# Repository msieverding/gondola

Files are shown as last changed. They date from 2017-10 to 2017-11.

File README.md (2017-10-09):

# gondola
## A parametric robot infrastructure for repeatable mobile experiments

This gondola was developed during a projet thesis at Graz University of Technology. This repository contains the following four main parts:
- Application Code for ESP8266 (/esp8266_controller)
- Printed circuit board (/esp8266_pcb)
- Some documentation and evaluation in .xls and .m files (/doc)
- 3D printed parts for this gondola (/3d_parts) copied from https://github.com/iprotonotarios/gondola

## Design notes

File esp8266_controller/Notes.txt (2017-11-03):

TODO:
- check all TODOs
- implement state for SW LED
- Application:
    - Add more freedom for applications, like section in EEPROM for configuration

Ideas:
- Use NTP for a time (maybe good for debug output, etc..). NTP is used here (https://github.com/Azure/azure-iot-arduino-protocol-http/blob/master/examples/simplesample_http/simplesample_http.ino)

Out of code documentation:
- Setup ATOM build environment
- Add libraries (https://www.youtube.com/watch?v=EBlHNBNHESQ)
- compiler optiization -O3 for maxium speed. Size does not matter on this chip

Unused libraries:
- PubSubClient
- AsyncMqttClient (https://github.com/marvinroger/async-mqtt-client)
  - 11.09.2017: Client recieves multiple messages and crashes.
  - MqTT server is very bad and neither server nor client fully supports QoS 2 and 3
- MqTT Server for ESP8266: https://github.com/FrancescoBaroneItaly/ME-MqTT-Server-for-ESP8266
  - Necessary to install certain libraries. They will show up as errors while building :D
  - Tutorial: http://bartech.mybluemix.net/2017/07/19/me-project-setup-mqtt-server-instance-on-esp8266/#more-828
- async MqTT Client used in MQTTClientAsync: (https://github.com/marvinroger/async-mqtt-client)
- use json? - JSON writer (https://github.com/maxpowel/ArduinoJsonWriter/blob/master/JsonWriter.cpp)
  - Unnecessary overhead -> not used. Binary protocoll

Used libraries:
- WebSocket Server and Cient (https://github.com/Links2004/arduinoWebSockets?utm_source=platformio&utm_medium=piohome)
 - Can use AsyncTCP with :https://github.com/me-no-dev/ESPAsyncTCP
 - see in readme of https://github.com/Links2004/arduinoWebSockets?utm_source=platformio&utm_medium=piohome
 - flag can be set in compiler (see platformio.ini)

Usefull sources:
- Linear regression: https://de.mathworks.com/help/matlab/data_analysis/linear-regression.html
- Paper about movement to optimize things: https://repository.tudelft.nl/islandora/object/uuid:aaecae50-6b30-40c3-accf-53302d200656/datastream/OBJ
- Exception decoder https://github.com/me-no-dev/EspExceptionDecoder

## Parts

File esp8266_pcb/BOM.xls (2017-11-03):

BOM – Gondola | No PCB's: | 3
Unit | per PCB | fixed | Total | Mouser Part No | Link
C1 | 1 | 0 | 3 | 667-EEE-FPV101XAP | http://www.mouser.at/ProductDetail/Panasonic/EEE-FPV101XAP/?qs=d1CqaRUMZD%2fZv%252bRM%2f4gWcQ%3d%3d
D1 | 1 | 0 | 3 | 821-1N4004 | http://www.mouser.at/ProductDetail/Taiwan-Semiconductor/1N4004/?qs=sGAEpiMZZMuMAfj%252bWfX4nEEHllp3mZcc
F1 | 1 | 0 | 3 | 652-MFR500 | http://www.mouser.at/ProductDetail/Bourns/MF-R500/
JP1 | 1 | 0 | 3 | 538-90131-0123 | http://www.mouser.at/ProductDetail/Molex/90131-0123/
Jumper | 3 | 0 | 9 | 571-530153-2 | http://www.mouser.at/ProductDetail/TE-Connectivity-AMP/530153-2/
LED | 5 | 0 | 15 | 604-APTD2012LQBCD | http://www.mouser.at/ProductDetail/Kingbright/APTD2012LQBC-D/
R1, R2 4,7k | 2 | 0 | 6 | 71-CRCW0805-4.7K-E3 | http://www.mouser.at/ProductDetail/Vishay/CRCW08054K70FKEA/
R3 1,2k | 1 | 0 | 3 | 756-PCF0805131K2BT1 | http://www.mouser.at/ProductDetail/Welwyn-Components-TT-Electronics/PCF0805-13-1K2BT1/
R4, R5 330 | 2 | 0 | 6 | 71-TNPW0805330RBEEA | http://www.mouser.at/ProductDetail/Vishay/TNPW0805330RBEEA/
R6, R7 100k | 2 | 0 | 6 | 588-AS08J1003ET | http://www.mouser.at/ProductDetail/Ohmite/AS08J1003ET/
S1 | 1 | 0 | 3 | 506-FSMCTTR | http://www.mouser.at/ProductDetail/TE-Connectivity-Alcoswitch/FSMCTTR/
A4988BREAKOUT | 1 | 0 | 3 |  | https://www.pololu.com/product/2133
A4899 Socket | 2 | 0 | 6 | 538-90147-1108 | http://www.mouser.at/ProductDetail/Molex/90147-1108/
ADAFRUIT_ESP8266 | 1 | 0 | 3 | 485-2471 | http://www.mouser.at/ProductDetail/Adafruit/2471/
ESP8266 Socket | 2 | 0 | 6 | 538-90147-1110 | http://www.mouser.at/ProductDetail/Molex/90147-1110/
DC DC | 1 | 0 | 3 | 755-BP5293-50 | http://www.mouser.at/ProductDetail/ROHM-Semiconductor/BP5293-50/
X1 | 1 | 0 | 3 | 651-1751248 | http://www.mouser.at/ProductDetail/Phoenix-Contact/1751248/
X2 | 1 | 0 | 3 | 651-1751264 | http://www.mouser.at/ProductDetail/Phoenix-Contact/1751264/
FTDI | 0 | 1 | 1 | 485-954 | http://www.mouser.at/ProductDetail/Adafruit/954/?qs=sGAEpiMZZMsMyYRRhGMFNg7907eNh002i%2fEnSsNEsb4%3d
Power Supply | 0 | 1 | 1 | 923-96PSAA36W12R1 | http://www.mouser.at/ProductDetail/Advantech/96PSA-A36W12R1/
Power Supply Cable | 0 | 1 | 1 | 364012-01 | http://www.mouser.at/ProductDetail/Qualtek/364012-01/?qs=sGAEpiMZZMvXcJVS4l7FP55o5eU9S9b7yWO1vi9Pexw%3d

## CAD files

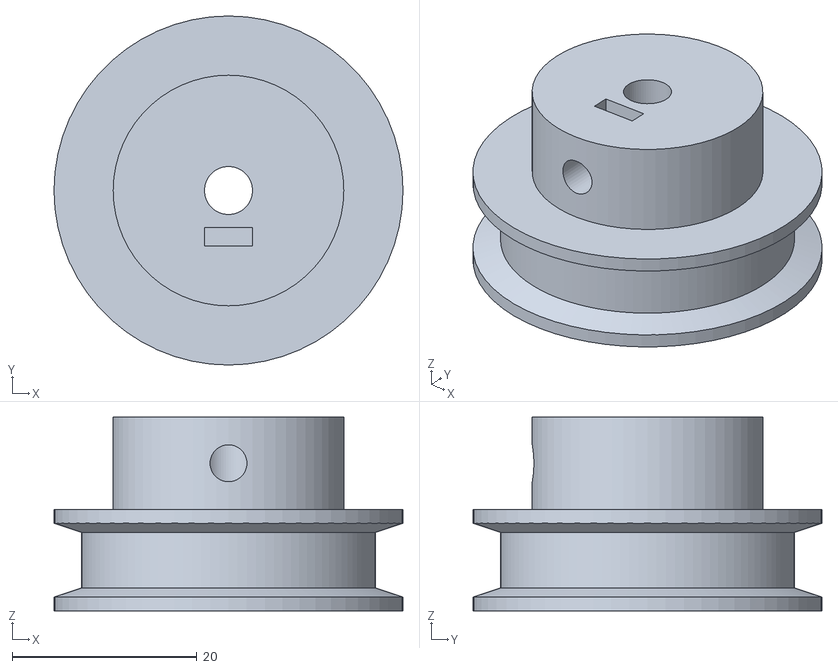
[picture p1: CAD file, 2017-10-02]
3d_parts/nema17_pulley.stl
37.8 x 37.8 x 21.0

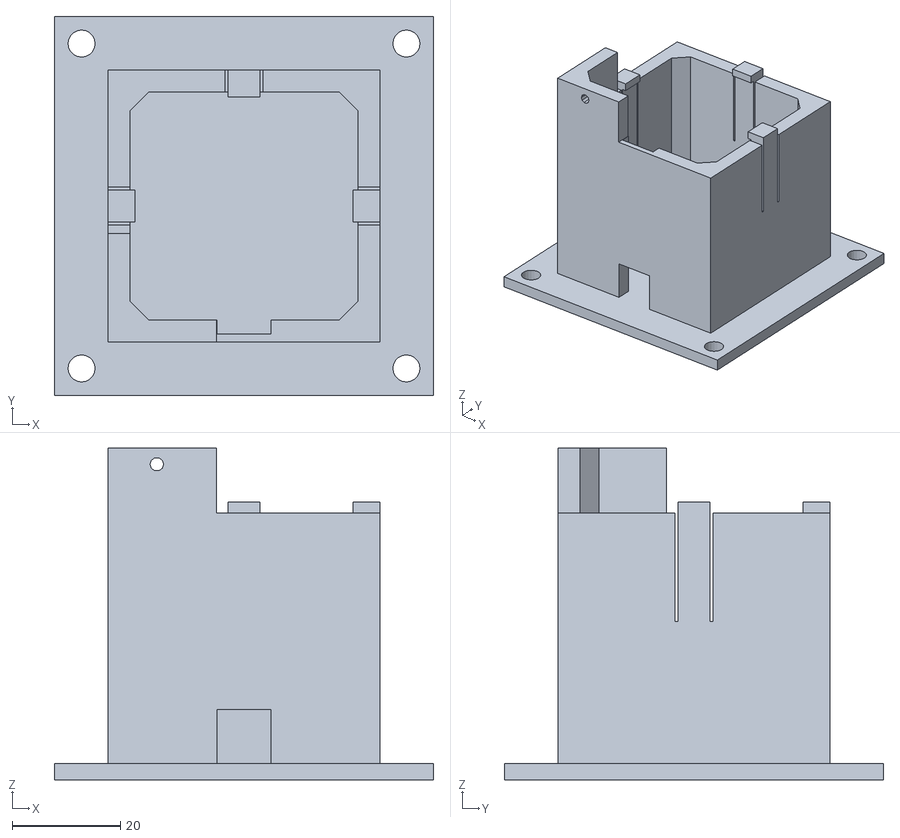
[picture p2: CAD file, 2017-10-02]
3d_parts/nema17_motor_base.stl
70.0 x 70.0 x 61.3

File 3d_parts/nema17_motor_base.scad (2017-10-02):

motorSide = 42.2;
motorHeight = 46.3;
motorMountingHoles = 31;
motorHolesLength = 4.5;

baseSide = 70;
baseHeight = 3;

wallWidth = 4;

// mounting base plate
difference()
{
    cube([baseSide, baseSide, baseHeight]);
    
    translate([5, 5, 0]) cylinder(d=5, h=baseHeight, $fn=20);
    translate([baseSide-5, 5, 0]) cylinder(d=5, h=baseHeight, $fn=20);
    translate([5, baseSide-5, 0]) cylinder(d=5, h=baseHeight, $fn=20);
    translate([baseSide-5, baseSide-5, 0]) cylinder(d=5, h=baseHeight, $fn=20);
    
}
// main enclosure
translate([(baseSide-motorSide)/2-wallWidth, (baseSide-motorSide)/2-wallWidth, baseHeight])
{
    difference()
    {
        union()
        {
            cube([motorSide+wallWidth*2, motorSide+wallWidth*2, motorHeight]);
            translate([0, 0, motorHeight])
            {
               difference()
               {
                   // thread hole and support
                   cube([20, 20, 12]);
                   translate([9, 0, 9]) rotate([-90, 0, 0]) cylinder(d=2.5, h=10, $fn=10);
               }
           }
       }
   
        
        translate([wallWidth+sqrt(2)*2.5, wallWidth, 0])
            minkowski()
            {
                cube([motorSide-sqrt(2)*5, motorSide-sqrt(2)*5, motorHeight]);
                rotate([0, 0, 45]) cube([5, 5, motorHeight]);
            }
         
        // latches   
        translate([motorSide/2+wallWidth-3.5, motorSide+wallWidth, motorHeight-20])        
            cube([0.5, wallWidth, 20]);
        translate([motorSide/2+wallWidth+3, motorSide+wallWidth, motorHeight-20])
            cube([0.5, wallWidth, 20]);
            
        translate([0, motorSide/2+wallWidth-3.5, motorHeight-20])
            cube([wallWidth, 0.5, 20]);
        translate([0, motorSide/2+wallWidth+3, motorHeight-20])
            cube([wallWidth, 0.5, 20]);
            
        translate([motorSide+wallWidth, motorSide/2+wallWidth-3.5, motorHeight-20])
            cube([wallWidth, 0.5, 20]);
        translate([motorSide+wallWidth, motorSide/2+wallWidth+3, motorHeight-20])
            cube([wallWidth, 0.5, 20]);
       
        // wire hole
        translate([motorSide/2+wallWidth-5, 0, 0])
            cube([10, wallWidth, 10]);
            
        // wire shaft
        translate([motorSide/2+wallWidth-5, wallWidth-2.5, 0])
            cube([10, 2.5, motorHeight]);
    }
    
    // latches top
    translate([motorSide/2+wallWidth-3, motorSide+wallWidth-1, motorHeight])
        cube([6, wallWidth+1, 2]);
    translate([0, motorSide/2+wallWidth-3, motorHeight])
        cube([wallWidth+1, 6, 2]);    
    translate([motorSide+wallWidth-1, motorSide/2+wallWidth-3, motorHeight])
        cube([wallWidth+1, 6, 2]);    
  
}

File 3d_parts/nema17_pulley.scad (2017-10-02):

innerDiameter = 2*50/PI;
outerDiameter = innerDiameter+6;

outerHeight = 11;
innerHeight = 8;
stepperShaftDiameter = 5.2; // default is 5, due to over-extrusion we had to change this; act accordingly 

//main pulley body
difference(){
    cylinder(d=outerDiameter, h=outerHeight, $fn=60);
    cylinder(d=stepperShaftDiameter, h=outerHeight, $fn=60);
    
    translate([0, 0, outerHeight/2-innerHeight/2]){
            
        difference(){
            translate([-outerDiameter/2, -outerDiameter/2, 0]) cube([outerDiameter, outerDiameter, innerHeight]);
            
            cylinder(r2=innerDiameter/2, r1=outerDiameter/2, h=1, $fn=100);
            translate([0, 0, 1]) cylinder(r=innerDiameter/2, h=innerHeight-2, $fn=100);
            translate([0, 0, innerHeight-1]) cylinder(r1=innerDiameter/2, r2=outerDiameter/2, h=1, $fn=100);
        }
    }
}

// locking screw and nut
translate([0, 0, outerHeight])
{
    difference()
    {
        cylinder(d=25, h=10, $fn=60);
        cylinder(d=stepperShaftDiameter, h=10, $fn=60);
        
        translate([0, 0, 5]) rotate([90, 0, 0]) cylinder(d=4, h=15, $fn=40);
        translate([-2.6, -6, 2.5]) cube([5.2, 2, 10]); 
    }
}

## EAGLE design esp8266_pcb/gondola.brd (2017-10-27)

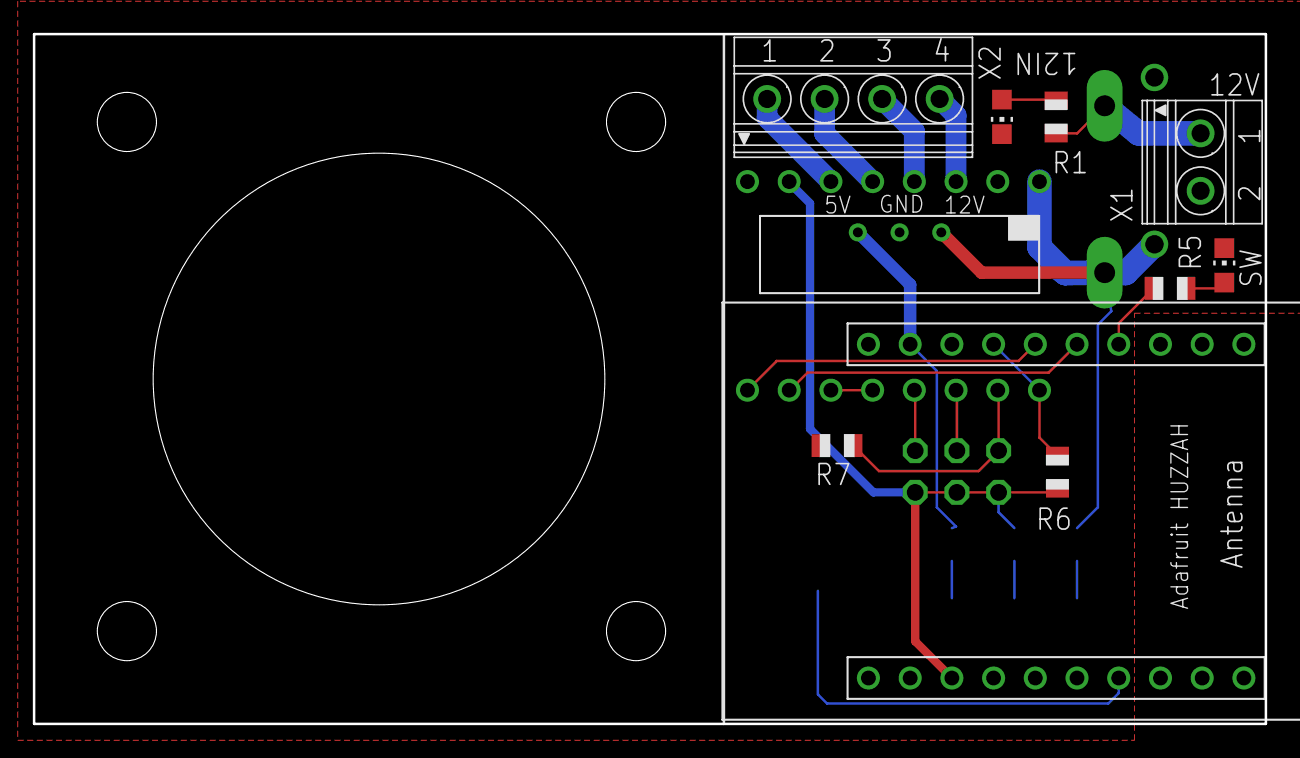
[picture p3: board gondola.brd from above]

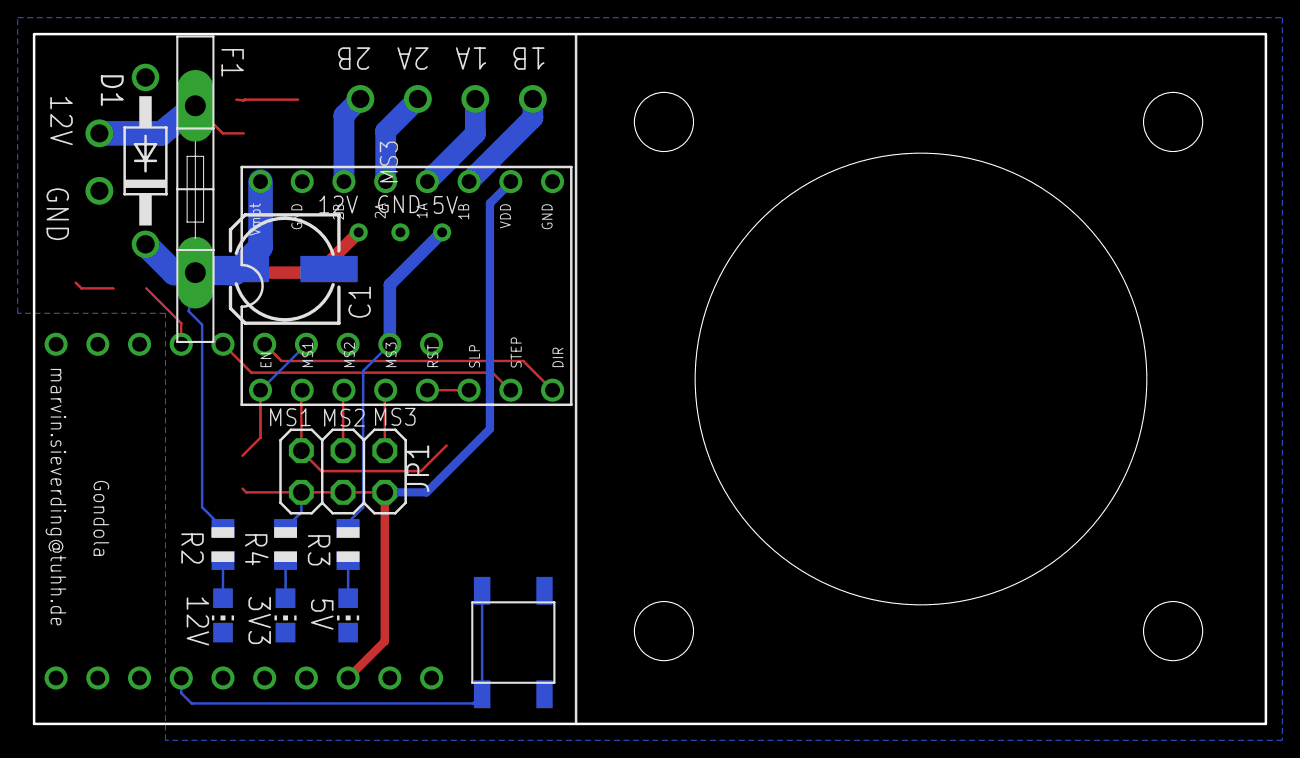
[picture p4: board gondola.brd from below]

Board: 2 copper layers, 75.0 x 42.0 mm, 22 parts (12 on the bottom side), 23 nets.

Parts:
C1: 100µF; 153CLV-0605
D1: 1N4004; DO41-10
F1: MFR500
JP1: 2X03
LED1_12IN, LED2_12V, LED3_5V, LED4_3V3, LED5_SW: CHIP-LED0805
R1, R2: 4.7k; R0805
R3: 1.2k; R0805
R4, R5: 330; R0805
R6, R7: 100k; R0805
U1: ROHM_BP5293-XX
U$1: A4988BREAKOUT
U$2: ADAFRUIT_ESP8266
U$4: FSMCTTR
X1: 1751248
X2: 1751264

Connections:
1A: U$1.1A, X2.2
1B: U$1.1B, X2.1
2A: U$1.2A, X2.3
2B: U$1.2B, X2.4
12V_IN: F1.P$1, R1.2, X1.1
!RESET: U$1.RST, U$1.SLP
+3V3: JP1.1, JP1.3, JP1.5, R4.2, R6.1, U$1.VDD, U$2.3_3V3
+5V: R3.2, U1.VOUT, U$2.9_VBAT
+12V: C1.+, D1.C, F1.P$2, R2.2, U1.VIN, U$1.VMOT
DIR: U$1.STEP, U$2.5_GPIO14
GND: C1.-, D1.A, LED1_12IN.C, LED2_12V.C, LED3_5V.C, LED4_3V3.C, LED5_SW.C, R7.2, U1.GND, U$1.GND, U$1.GND@0, U$2.1_GND, U$2.10_GND, U$4.1, U$4.2, X1.2
MS1: JP1.2, R7.1, U$1.MS1
MS2: JP1.4, U$1.MS2
MS3: JP1.6, U$1.MS3
M_EN: R6.2, U$1.EN, U$2.7_GPIO13
unnamed: LED2_12V.A, R2.1
unnamed: LED1_12IN.A, R1.1
unnamed: LED4_3V3.A, R4.1
unnamed: LED5_SW.A, R5.1
unnamed: LED3_5V.A, R3.1
STEP: U$1.DIR, U$2.6_GPIO12
SW_BUT: U$2.7_GPIO4, U$4.3, U$4.4
SW_LED: R5.2, U$2.4_GPIO16

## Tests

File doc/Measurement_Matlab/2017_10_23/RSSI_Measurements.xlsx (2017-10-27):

Algorithm 1 - Sampling
x | y | RSSI
RUN | 1
40 | 50 | -55
40 | 150 | -62
40 | 250 | -49
40 | 225 | -53
40 | 250 | -51
40 | 275 | -55
40 | 250
RUN | 2
40 | 50 | -55
40 | 150 | -50
40 | 250 | -48
40 | 225 | -47
40 | 250 | -49
40 | 275 | -58
40 | 225
Algorithm 2 - Random Walk
RUN | 1
40 | 225 | -50
40 | 215 | -49
40 | 205 | -48
40 | 195 | -50
40 | 205 | -49
40 | 215 | -48
40 | 225 | -49
40 | 215
40 | 215 | -47
40 | 205 | -49
40 | 215 | -47
40 | 225 | -49
40 | 215
40 | 50 | -55
40 | 40 | -56
40 | 50 | -57
40 | 60 | -52
40 | 70 | -52
40 | 80 | -52
40 | 90 | -59
40 | 80
40 | 80 | -52
40 | 70 | -49
40 | 60 | -52
40 | 70 | -49
40 | 80 | -56
40 | 70
Algorithm 1 - Sampling with better grid
RUN 1
40 | 50 | -56
40 | 100 | -59
40 | 150 | -52
40 | 200 | -51
40 | 250 | -50
40 | 225 | -48
40 | 240 | -49
40 | 250 | -49
40 | 260 | -49
40 | 275 | -55
40 | 225
RUN 2
40 | 50 | -56
40 | 100 | -54
40 | 150 | -57
40 | 200 | -49
40 | 250 | -48
40 | 225 | -49
40 | 240 | -48
40 | 250 | -49
40 | 260 | -53
40 | 275 | -50
40 | 240

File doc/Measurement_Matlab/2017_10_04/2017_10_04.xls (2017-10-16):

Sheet: 01
Offset X | 2364 | Offset Y | 1200 |  | 2D Messung als verifizierung des codes
Punkt | X | Y | Meas X | Meas Y | Dist X | Dist Y | Err X | Err Y | abs(Err)
0 | 400 | 1500 | 1964 | 2700 | 400 | 1500 | 0 | 0 | 0.00
1 | 400 | 1200 |  |  | 405 | 1798 | -5 | 598 | 598.02
2 | 400 | 900 |  |  | 2364 | -1200 | -1964 | -2100 | 2875.29
3 | 400 | 600 |  |  | 2364 | -1200 | -1964 | -1800 | 2664.08
4 | 400 | 300 |  |  | 2364 | -1200 | -1964 | -1500 | 2471.29
5 | 400 | 1800 | 1959 | 2998 | 405 | 1798 | -5 | -2 | 5.39
6 | 400 | 2100 | 1967 | 3294 | 397 | 2094 | 3 | -6 | 6.71
7 | 400 | 2400 | 1969 | 3595 | 395 | 2395 | 5 | -5 | 7.07
8 | 400 | 2700 |  |  | 2364 | -1200 | -1964 | -3900 | 4366.61
9 | 400 | 3000 |  |  | 2364 | -1200 | -1964 | -4200 | 4636.52
10 | 800 | 1500 |  |  | 2364 | -1200 | -1564 | -2700 | 3120.27
11 | 800 | 1200 |  |  | 2364 | -1200 | -1564 | -2400 | 2864.63
12 | 800 | 900 |  |  | 2364 | -1200 | -1564 | -2100 | 2618.41
13 | 800 | 600 |  |  | 2364 | -1200 | -1564 | -1800 | 2384.55
14 | 800 | 300 |  |  | 2364 | -1200 | -1564 | -1500 | 2167.05
15 | 800 | 1800 |  |  | 2364 | -1200 | -1564 | -3000 | 3383.21
16 | 800 | 2100 |  |  | 2364 | -1200 | -1564 | -3300 | 3651.86
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

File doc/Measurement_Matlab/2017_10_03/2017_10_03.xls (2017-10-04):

OffsetX | 2364
OffsetY | 1200
OffsetZ | 5
crash
1 | startMeas | start | Input | endMeas | end
x | 1618 | 746 | 746 | 1607 | 757 | 11
y | 3686 | 2486 | 1486 | 2691 | 1491 | 5
z | 759 | 754 | 745 | 761 | 756 | 11
2 | startMeas | start | Input | endMeas | end
x | 1607 | 757 | 746 | 1557 | 807 | 61
y | 2691 | 1491 | 1486 | 1487 | 1487 | 1
z | 761 | 756 | 1745 | 1760 | 1755 | 10
3 | startMeas | start | Input | endMeas | end
x | 1557 | 807 | 807 | 1579 | 785 | -22
y | 1487 | 1487 | 487 | 506 | 506 | 19
z | 1760 | 1755 | 1755 | 1763 | 1758 | 3
4 | startMeas | start | Input | endMeas | end
x | 1579 | 785 | 785 | 1571 | 793 | 8
y | 506 | 506 | 1006 | 995 | 995 | -11
z | 1763 | 1758 | 1758 | 1767 | 1762 | 4
5 | startMeas | start | Input | endMeas | end
x | 1571 | 793 | 793 | 1585 | 779 | -14
y | 995 | 995 | 995 | 984 | 984 | -11
z | 1767 | 1762 | 2762 | 2769 | 2764 | 2
6 | startMeas | start | Input | endMeas | end
x | 1585 | 779 | 779 | 1597 | 767 | -12
y | 984 | 984 | 984 | 2147 | 947 | -37
z | 2769 | 2764 | 3764 | 3759 | 3754 | -10
7 | startMeas | start | Input | endMeas | end
x | 1597 | 767 | 767 | 1584 | 780 | 13
y | 2147 | 947 | 1947 | 3121 | 1921 | -26
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

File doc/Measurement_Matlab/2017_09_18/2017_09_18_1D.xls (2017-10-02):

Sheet: 01
1D Measurements
Spooled mm | Speed cm/s | Meas 1 mm | Meas 2 mm | Meas 3 mm | Mean mm | Distance Total | Err Total mm | Err %target traveled distance
0 |  | 1248 | 1248 | 1248 | 1248.0 | 0.00 | 0.00
100 | 5 | 1150 | 1149 | 1148 | 1149.0 | 99.00 | -1.00 | -1.00%
200 | 5 | 1047 | 1047 | 1047 | 1047.0 | 201.00 | 1.00 | 0.50%
300 | 5 | 946 | 946 | 945 | 945.7 | 302.33 | 2.33 | 0.78%
400 | 5 | 844 | 844 | 844 | 844.0 | 404.00 | 4.00 | 1.00%
500 | 5 | 741 | 742 | 741 | 741.3 | 506.67 | 6.67 | 1.33%
600 | 5 | 639 | 639 | 649 | 642.3 | 605.67 | 5.67 | 0.94%
700 | 5 | 538 | 538 | 539 | 538.3 | 709.67 | 9.67 | 1.38%
800 | 5 | 438 | 438 | 436 | 437.3 | 810.67 | 10.67 | 1.33%
900 | 5 | 337 | 336 | 336 | 336.3 | 911.67 | 11.67 | 1.30%
1000 | 5 | 235 | 235 | 234 | 234.7 | 1013.33 | 13.33 | 1.33%
900 | 5 | 336 | 337 | 335 | 336.0 | 912.00 | 12.00 | 1.33%
800 | 5 | 436 | 436 | 436 | 436.0 | 812.00 | 12.00 | 1.50%
700 | 5 | 534 | 534 | 534 | 534.0 | 714.00 | 14.00 | 2.00%
600 | 5 | 638 | 639 | 637 | 638.0 | 610.00 | 10.00 | 1.67%
500 | 5 | 738 | 739 | 740 | 739.0 | 509.00 | 9.00 | 1.80%
400 | 5 | 841 | 840 | 840 | 840.3 | 407.67 | 7.67 | 1.92%
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

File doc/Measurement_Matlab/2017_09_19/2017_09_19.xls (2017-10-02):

1D Measurements
Spooled mm | Speed cm/s | Meas 1 mm | Meas 2 mm | Meas 3 mm | Mean mm | Distance Total | Err Total mm | Err % | Single movement total error [mm]
0 |  | 282 | 283 | 283 | 282.7 | 0.00 | 0.00
200 | 1 | 485 | 486 | 486 | 485.7 | 203.00 | 3.00 | 1.50% | 3.00
400 | 1 | 690 | 690 | 689 | 689.7 | 407.00 | 7.00 | 1.75% | 4.00
600 | 1 | 892 | 893 | 893 | 892.7 | 610.00 | 10.00 | 1.67% | 3.00
800 | 1 | 1095 | 1095 | 1095 | 1095.0 | 812.33 | 12.33 | 1.54% | 2.33
1000 | 1 | 1299 | 1299 | 1299 | 1299.0 | 1016.33 | 16.33 | 1.63% | 4.00
1200 | 1 | 1500 | 1502 | 1502 | 1501.3 | 1218.67 | 18.67 | 1.56% | 2.33
1400 | 1 | 1703 | 1705 | 1705 | 1704.3 | 1421.67 | 21.67 | 1.55% | 3.00
1600 | 1 | 1908 | 1909 | 1908 | 1908.3 | 1625.67 | 25.67 | 1.60% | 4.00
1800 | 1 | 2106 | 2108 | 2109 | 2107.7 | 1825.00 | 25.00 | 1.39% | -0.67
2000 | 1 | 2313 | 2312 | 2313 | 2312.7 | 2030.00 | 30.00 | 1.50% | 5.00
2200 | 1 | 2512 | 2515 | 2515 | 2514.0 | 2231.33 | 31.33 | 1.42% | -1.33
2400 | 1 | 2716 | 2717 | 2715 | 2716.0 | 2433.33 | 33.33 | 1.39% | -2.00
2600 | 1 | 2916 | 2918 | 2916 | 2916.7 | 2634.00 | 34.00 | 1.31% | -0.67
2800 | 1 | 3119 | 3117 | 3121 | 3119.0 | 2836.33 | 36.33 | 1.30% | -2.33
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

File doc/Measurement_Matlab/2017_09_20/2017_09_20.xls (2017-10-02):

Offset X | 2364 | Offset Y | 1200
Punkt | X | Y | Meas X | Meas Y | Dist X | Dist Y | Err X | Err Y | abs(Err)
0 | 400 | 1500 | 1964 | 2700 | 400 | 1500 | 0 | 0 | 0.00
1 | 400 | 1200 | 1981 | 2394 | 383 | 1194 | 17 | -6 | 18.03
2 | 400 | 900 | 1989 | 2085 | 375 | 885 | 25 | -15 | 29.15
3 | 400 | 600 | 1996 | 1777 | 368 | 577 | 32 | -23 | 39.41
4 | 400 | 300 | 2005 | 1483 | 359 | 283 | 41 | -17 | 44.38
5 | 400 | 1800 | 1956 | 3004 | 408 | 1804 | -8 | 4 | 8.94
6 | 400 | 2100 | 1948 | 3311 | 416 | 2111 | -16 | 11 | 19.42
7 | 400 | 2400 | 1945 | 3622 | 419 | 2422 | -19 | 22 | 29.07
8 | 400 | 2700 | 1958 | 3930 | 406 | 2730 | -6 | 30 | 30.59
9 | 400 | 3000 | 1969 | 4236 | 395 | 3036 | 5 | 36 | 36.35
10 | 800 | 1500 | 1558 | 2704 | 806 | 1504 | -6 | 4 | 7.21
11 | 800 | 1200 | 1562 | 2394 | 802 | 1194 | -2 | -6 | 6.32
12 | 800 | 900 | 1567 | 2084 | 797 | 884 | 3 | -16 | 16.28
13 | 800 | 600 | 1578 | 1780 | 786 | 580 | 14 | -20 | 24.41
14 | 800 | 300 | 1588 | 1477 | 776 | 277 | 24 | -23 | 33.24
15 | 800 | 1800 | 1565 | 3006 | 799 | 1806 | 1 | 6 | 6.08
16 | 800 | 2100 | 1563 | 3313 | 801 | 2113 | -1 | 13 | 13.04
17 | 800 | 2400 | 1564 | 3622 | 800 | 2422 | 0 | 22 | 22.00
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

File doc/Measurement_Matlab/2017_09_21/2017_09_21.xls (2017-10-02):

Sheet: 01
Offset X | 2364 | Offset Y | 1200 |  | Measurement without any corrections
Punkt | X | Y | Meas X | Meas Y | Dist X | Dist Y | Err X | Err Y | abs(Err)
0 | 400 | 1500 | 1964 | 2700 | 400 | 1500 | 0 | 0 | 0.00
1 | 400 | 1200 | 1979 | 2396 | 385 | 1196 | 15 | -4 | 15.52
2 | 400 | 900 | 1989 | 2095 | 375 | 895 | 25 | -5 | 25.50
3 | 400 | 600 | 1994 | 1790 | 370 | 590 | 30 | -10 | 31.62
4 | 400 | 300 | 2001 | 1488 | 363 | 288 | 37 | -12 | 38.90
5 | 400 | 1800 | 1956 | 3004 | 408 | 1804 | -8 | 4 | 8.94
6 | 400 | 2100 | 1947 | 3311 | 417 | 2111 | -17 | 11 | 20.25
7 | 400 | 2400 | 1952 | 3619 | 412 | 2419 | -12 | 19 | 22.47
8 | 400 | 2700 | 1956 | 3930 | 408 | 2730 | -8 | 30 | 31.05
9 | 400 | 3000 | 1969 | 4234 | 395 | 3034 | 5 | 34 | 34.37
10 | 800 | 1500 | 1564 | 2698 | 800 | 1498 | 0 | -2 | 2.00
11 | 800 | 1200 | 1570 | 2394 | 794 | 1194 | 6 | -6 | 8.49
12 | 800 | 900 | 1575 | 2090 | 789 | 890 | 11 | -10 | 14.87
13 | 800 | 600 | 1581 | 1784 | 783 | 584 | 17 | -16 | 23.35
14 | 800 | 300 | 1591 | 1480 | 773 | 280 | 27 | -20 | 33.60
15 | 800 | 1800 | 1557 | 3009 | 807 | 1809 | -7 | 9 | 11.40
16 | 800 | 2100 | 1552 | 3311 | 812 | 2111 | -12 | 11 | 16.28
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

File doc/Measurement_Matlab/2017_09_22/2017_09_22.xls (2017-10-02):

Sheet: 01
Offset | 0 | mm
TotalLength | 10000 | mm
Length [mm] | Meas[mm]
0 | 0
500 | 526
1000 | 1053
1500 | 1575 | 504
2000 | 2103 | 1032
2500 | 2619 | 1548
3000 | 3141 | 2070
3500 | 3663 | 2592
4000 | 4170 | 3099
4500 | 4684 | 3613
5000 | 5200 | 4129
5500 | 5710 | 4639
6000 | 6221 | 5150
6500 | 6731 | 5660
7000 | 7233 | 6162
7500 | 7750 | 6679
8000 | 8251 | 7180
8500 | 8761 | 7690
9000 | 9283 | 8212

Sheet: 02
Offset | 0 | mm
TotalLength | 10000 | mm |  | Used Correction set:
Length [mm] | Meas[mm] |  |  | float b0 = -0.000024216423411; float b1 = 0.051005307386112; float b2 = 0.472932330827063;
0 | 0
500 | 499
1000 | 991
1500 | 1480 | 423 | An diesem Punkte wurde das Seil über einen Haken gelegt und
2000 | 1986 | 929 | dann ab dem Haken gemessen. Der Rest wurde dann als
2500 | 2483 | 1426 | Offset draufgerechnet
3000 | 2987 | 1930
3500 | 3482 | 2425
4000 | 3998 | 2941
4500 | 4487 | 3430
5000 | 4987 | 3930
5500 | 5495 | 4438
6000 | 5997 | 4940
6500 | 6496 | 5439
7000 | 6999 | 5942
7500 | 7502 | 6445
8000 | 8003 | 6946
8500 | 8515 | 7458
9000 | 9017 | 7960
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

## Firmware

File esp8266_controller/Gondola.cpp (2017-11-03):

#include <Arduino.h>
#include "config.hpp"
#include "Log.hpp"
#include "Gondola.hpp"
#include "CommandInterpreter.hpp"

Gondola::Gondola()
 : m_CurrentPosition(Config::get()->getGO_POSITION())
 , m_TargetPosition(m_CurrentPosition)
 , m_AnchorList()
 , m_UnfinishedAnchors(0)
 , m_TravelTime(0)
 , m_StartTime(0)
{
  logDebug("Creating gondola at: %s\n", m_CurrentPosition.toString().c_str());
  CommandInterpreter::get()->addCommand("move", std::bind(&Gondola::moveCommand, this, std::placeholders::_1));
}

Gondola::~Gondola()
{
  CommandInterpreter::get()->deleteCommand("move");
  std::list<IAnchor *>::iterator it = m_AnchorList.begin();
  while (it != m_AnchorList.end())
  {
    logDebug("Delete Anchor %d from list\n", (*it)->getID());
    deleteAnchor(it++);
  }
}

void Gondola::setInitialPosition(Coordinate position)
{
  m_CurrentPosition = position;
  m_TargetPosition = position;
  std::list<IAnchor *>::iterator it = m_AnchorList.begin();
  while (it != m_AnchorList.end())
  {
    IAnchor *anchor = *it;
    if (anchor->getID() != HW_ANCHOR_ID)
    {
      float spooledDistance = calculateCorrectedSpooling(anchor, Coordinate::euclideanDistance(anchor->getAnchorPos(), m_CurrentPosition));
      if (anchor->setInitialSpooledDistance(spooledDistance) == false)
      {
        logWarning("Unable to init anchor %d. No Connection available. Delete it from Gondola.\n", anchor->getID());
        deleteAnchor(it++);
        continue;
      }
    }
    it++;
  }
}

void Gondola::addAnchor(IAnchor *anchor)
{
  float spooledDistance = calculateCorrectedSpooling(anchor, Coordinate::euclideanDistance(anchor->getAnchorPos(), m_CurrentPosition));
  anchor->setInitialSpooledDistance(spooledDistance);
  m_AnchorList.push_front(anchor);        // push new (remote) anchors to the front, so that the hardware anchor starts to spool after the message to the remote anchors was delivered (better synchronisation during spooling)
}

void Gondola::deleteAnchor(std::list<IAnchor *>::iterator it)
{
  IAnchor *anchor = *it;
  if (anchor->getID() != HW_ANCHOR_ID)
  {
    delete(anchor);
  }
  logDebug("Erase Anchor %d from list\n", anchor->getID());
  m_AnchorList.erase(it);
}

void Gondola::deleteAnchor(uint8_t id)
{
  std::list<IAnchor *>::iterator it = m_AnchorList.begin();
  while (it != m_AnchorList.end())
  {
    IAnchor *anchor = *it;
    if (anchor->getID() == id)
    {
      deleteAnchor(it++);
      continue;
    }
    it++;
  }
}

void Gondola::reportAnchorFinished(uint8_t id)
{
  logVerbose("Anchor '%d' finished moving\n", id);
  std::list<IAnchor *>::iterator it;
  for (it = m_AnchorList.begin(); it != m_AnchorList.end(); it++)
  {
    IAnchor *anchor = *it;
    if (anchor->getID() == id)
    {
      noInterrupts();
      m_UnfinishedAnchors &= ~(1 << anchor->getID());
      interrupts();
    }
  }
  checkForReady();
}

Coordinate Gondola::getCurrentPosition()
{
  return m_CurrentPosition;
}

Coordinate Gondola::getTimeEstimatedPosition()
{
  uint32_t travelTime = millis() - m_StartTime;

  if (travelTime > m_TravelTime)
    return m_CurrentPosition;

  float travelPerCent = ((float)travelTime) / m_TravelTime;

  Coordinate estimatedPosition;
  estimatedPosition.x = m_CurrentPosition.x + (m_TargetPosition.x - m_CurrentPosition.x) * travelPerCent;
  estimatedPosition.y = m_CurrentPosition.y + (m_TargetPosition.y - m_CurrentPosition.y) * travelPerCent;
  estimatedPosition.z = m_CurrentPosition.z + (m_TargetPosition.z - m_CurrentPosition.z) * travelPerCent;

  return estimatedPosition;
}

Coordinate Gondola::getTargetPosition()
{
  return m_TargetPosition;
}

uint32_t Gondola::getTravelTime()
{
  return m_TravelTime;
}

void Gondola::setTargetPosition(Coordinate &targetPos, float &speed)
{
  m_TargetPosition = targetPos;
  if (speed == 0.0f)
    speed = 1.0f;

  logDebug("Move to: %s\n", targetPos.toString().c_str());

  float travelDistance = Coordinate::euclideanDistance(m_CurrentPosition, m_TargetPosition);
  if (travelDistance == 0)
  {
    logVerbose("Travel distance = 0. Nothing to do.\n");
    return;
  }

  float travelTime = travelDistance / speed;
  logVerbose("TravelDistance: %s, TravelTime: %s\n", FTOS(travelDistance), FTOS(travelTime));
  uint32_t maxSteps = 0;

  // prepare to spool
  std::list<IAnchor *>::iterator it;
  for (it = m_AnchorList.begin(); it != m_AnchorList.end(); it++)
  {
    uint32_t stepsTodo;
    IAnchor *anchor = *it;
    float targetSpooledDistance = Coordinate::euclideanDistance(anchor->getAnchorPos(), targetPos);

    float correctedSpooledDistance = calculateCorrectedSpooling(anchor, targetSpooledDistance);
    stepsTodo = anchor->setTargetSpooledDistance(correctedSpooledDistance);
    logVerbose("targetSpooledDistance: %s, correctedSpooledDistance: %s\n", FTOS(targetSpooledDistance), FTOS(correctedSpooledDistance));

    maxSteps = std::max(maxSteps, stepsTodo);
  }

  // TODO change value of 1000.0f to a realistic one
  logVerbose("Budget: %ss, Minimum %ss\n\n", FTOS(travelTime), FTOS(maxSteps / 1000.0f));

  travelTime = std::max(travelTime, maxSteps / 1000.0f);
  travelTime *= 1000;
  m_TravelTime = static_cast<uint32_t>(travelTime);

  it = m_AnchorList.begin();
  while (it != m_AnchorList.end())
  {
    IAnchor *anchor = *it;
    m_UnfinishedAnchors |= (1 << anchor->getID());
    if (anchor->startMovement(m_TravelTime) == false)
    {
      logWarning("No connection to anchor %d possible. Delete anchor from list.\n", anchor->getID());
      deleteAnchor(it++);
      continue;
    }
    it++;
  }
  m_StartTime = millis();
}

std::list<IAnchor *> Gondola::getAnchorList(void)
{
  return m_AnchorList;
}

bool Gondola::isIdle()
{
  return m_UnfinishedAnchors == 0;
}

bool Gondola::moveCommand(std::string &s)
{
  CommandInterpreter *CI = CommandInterpreter::get();
  uint8_t args = CI->getNumArgument(s);
  Coordinate newPosition;
  float speed;

  if(args != 4)
  {
    logWarning("Unsupported!\n");
    logWarning("Usage: move x y z s\n");
    logWarning("\tx - float for x coordinate (e.g. 1.0)\n");
    logWarning("\ty - float for y coordinate (e.g. 1.0)\n");
    logWarning("\tz - float for z coordinate (e.g. 1.0)\n");
    logWarning("\ts - float for speed (e.g. 1.0)\n");
    return false;
  }
  std::string arg;
  CI->getArgument(s, arg, 0);
  newPosition.x = atof(arg.c_str());
  CI->getArgument(s, arg, 1);
  newPosition.y = atof(arg.c_str());
  CI->getArgument(s, arg, 2);
  newPosition.z = atof(arg.c_str());
  CI->getArgument(s, arg, 3);
  speed = atof(arg.c_str());

  setTargetPosition(newPosition, speed);
  return true;
}

void Gondola::checkForReady()
{
  if (m_UnfinishedAnchors == 0)
  {
    m_CurrentPosition = m_TargetPosition;
    Config::get()->setGO_POSITION(m_CurrentPosition);
    Config::get()->writeGOToEEPROM(true);
  }
}

float Gondola::calculateCorrectedSpooling(IAnchor *anchor, float targetSpooledDistance)
{
  // Err = b0 * realSpooledRope^2 + b1 * realSpooledRope + b2
  float b0 = -0.000024216423411;
  float b1 = 0.051005307386112;
  float b2 = 0.472932330827063;
  float ropeOffset = anchor->getRopeOffset();
  // Error at coordinate zero
  float estimatedErrZero = b0 * ropeOffset * ropeOffset + b1 * ropeOffset + b2;
  float ropeSpooledAtTarget = ropeOffset + targetSpooledDistance;
  // Error at target coordinate
  float estimatedErrTarget = b0 * ropeSpooledAtTarget * ropeSpooledAtTarget + b1 * ropeSpooledAtTarget + b2;
  // Estimated Error in movement
  float estimatedErr = estimatedErrTarget - estimatedErrZero;
  float correctedDistance = targetSpooledDistance - estimatedErr;

  logVerbose("Err estimation: estimatedErrZero: %s, estimatedErrTarget %s, estimatedErr %s\n", FTOS(estimatedErrZero), FTOS(estimatedErrTarget), FTOS(estimatedErr));
  logVerbose("Err estimation: targetSpooledDistance: %s, correctedDistance: %s\n", FTOS(targetSpooledDistance), FTOS(correctedDistance));
  return correctedDistance;
}

IAnchor *Gondola::getAnchor(uint8_t id)
{
  std::list<IAnchor *>::iterator it = m_AnchorList.begin();
  while (it != m_AnchorList.end())
  {
    IAnchor *anchor = *it;
    if (anchor->getID() == id)
    {
      return anchor;
    }
    it++;
  }
  return NULL;
}

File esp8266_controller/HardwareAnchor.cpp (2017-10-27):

#include "HardwareAnchor.hpp"
#include "Log.hpp"

HardwareAnchor *s_MoveInstance = NULL;

HardwareAnchor::HardwareAnchor(uint8_t id)
 : IAnchor(id, Config::get()->getGO_ANCHORPOS(), 0.0f , 0.0f, Config::get()->getGO_ROPEOFFSET())
 , m_Pins({13, 14, 12})
 , m_StepsTodo(0)
 , m_StepsDone(0)
 , m_Direction(1)
 , m_MovementFinished(false)
 , m_Timer()
{
  logDebug("Creating HardwareAnchor at (%s) with a spooled offset of (%s)\n", m_AnchorPosition.toString().c_str(), FTOS(m_RopeOffset));
  configurePins();
  s_MoveInstance = this;
}

HardwareAnchor::~HardwareAnchor()
{
  s_MoveInstance = NULL;
}

float HardwareAnchor::getTimeEstimatedSpooledDistance()
{
  // We don't need to estimate it. WE know it exactly.
  return getSpooledDistance();
}

uint32_t HardwareAnchor::setTargetSpooledDistance(float targetDistance)
{
  float distanceTodo = targetDistance - m_SpooledDistance;
  distanceTodo = roundPrecision(distanceTodo, MIN_PRECISION);   // round to a given precision (1 step)
  m_TargetSpooledDistance = m_SpooledDistance + distanceTodo;

  logVerbose("Anchor ID: %d on position: %s\n", m_ID, m_AnchorPosition.toString().c_str());
  logVerbose("Spooled: %scm, Delta: %scm\n", FTOS(m_SpooledDistance), FTOS(distanceTodo));

  if (distanceTodo < 0)
  {
    digitalWrite(m_Pins.dir, LOW);
    m_Direction = -1;
    distanceTodo = abs(distanceTodo);
  }
  else
  {
    digitalWrite(m_Pins.dir, HIGH);
    m_Direction = 1;
  }
  // calculate number of steps todo
  m_StepsTodo = distanceTodo * STEP_CM;

  logVerbose("Rounded to: (%scm): %scm, steps: %ld, microsteps: %ld\n\n", floatToString(MIN_PRECISION).c_str(), floatToString(distanceTodo).c_str(), m_StepsTodo, m_StepsTodo * MICROSTEPS);

  m_StepsTodo *= MICROSTEPS; // we need to account for all microsteps
  m_StepsDone = 0;

  return m_StepsTodo;
}

bool HardwareAnchor::startMovement(uint32_t traveltime)
{
  IAnchor::startMovement(traveltime);
  logVerbose("Start: %d\n", millis());
  m_Timer.attach_ms(1, move);
  return true;
}

void HardwareAnchor::configurePins()
{
  pinMode(m_Pins.en, OUTPUT);
  pinMode(m_Pins.stp, OUTPUT);
  pinMode(m_Pins.dir, OUTPUT);
  digitalWrite(m_Pins.en, LOW);
}

inline void HardwareAnchor::startStep()
{
  digitalWrite(m_Pins.stp, HIGH);   // start stepp trigger
}

inline void HardwareAnchor::endStep()
{
  digitalWrite(m_Pins.stp, LOW);    // stop step trigger
}

void HardwareAnchor::move()
{
  uint32_t stepsGoal = ceil(((float)((millis() - s_MoveInstance->m_StartTime) * s_MoveInstance->m_StepsTodo)) / s_MoveInstance->m_TravelTime);
  if (stepsGoal > s_MoveInstance->m_StepsTodo)
    stepsGoal = s_MoveInstance->m_StepsTodo;

  while (s_MoveInstance->m_StepsDone < stepsGoal)
  {
    s_MoveInstance->startStep();
    delayMicroseconds(10); // delay to be sure that the step was done
    s_MoveInstance->endStep();
    delayMicroseconds(10); // delay to be sure that the step was done
    s_MoveInstance->m_SpooledDistance += s_MoveInstance->m_Direction * (1.0f / STEP_CM / MICROSTEPS);
    s_MoveInstance->m_StepsDone++;
  }

  if (s_MoveInstance->m_StepsDone == s_MoveInstance->m_StepsTodo)
  {
    s_MoveInstance->m_MovementFinished = true;
    s_MoveInstance->m_Timer.detach();
  }
}

void HardwareAnchor::loop()
{
  if (m_MovementFinished == true)
  {
    m_MovementFinished = false;
    m_StartTime = 0;
    executeReadyCallback();
    logVerbose("Finish: %d, m_SpooledDistance=%s.\n", millis(), FTOS(m_SpooledDistance));
  }
}

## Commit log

2017-10-02 initial commit
    base repository: msieverding/gondola_arduino (forked from iprotonotarios/gondola)
    commit id: db645ba253deac1991805521f588c15f09427886
    [BOM.xls, gondola.brd, gondola.sch, gondola_old.brd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]
2017-10-02 add measurements and matlab evaluation
    [2017_09_18_1D.xls, 2017_09_19.xls, 2017_09_20.xls, 2017_09_21.xls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]
2017-10-02 updated BOM
    [BOM.xls]
2017-10-04 added measurements from today and yesterday
    [2017_10_03.xls, 2017_10_04.xls]
2017-10-05 Added seconds measurement to 2017_10_04_02 and added grid plots to the error models
    [2017_10_04.xls]
2017-10-16 added force
    [2017_10_04.xls]
2017-10-27 deleted old layout. Corrected footbrint of button. Changed pins to Adafruit HUZZAH. Added RSSI measurements
    [BOM.xls, RSSI_Measurements.xlsx, gondola.brd, gondola.sch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]
2017-11-03 added missing documentation and updated doxygen ouput
    [BOM.xls]
